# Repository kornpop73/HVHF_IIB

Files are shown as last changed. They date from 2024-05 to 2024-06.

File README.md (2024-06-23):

# HVHF_IIB
* Single-ended 65Vpp, 5ns amplifier with multiple output stages capable of driving capacitive loads up to 100pF. 
* This design is based on the circuit described in the 2005 paper by Holger Müller titled 'Fast High-Voltage Amplifiers for Driving Electro-Optic Modulators'.
* A link to the original paper can be found at the bottom of this page.
# High Voltage High Frequency IIB
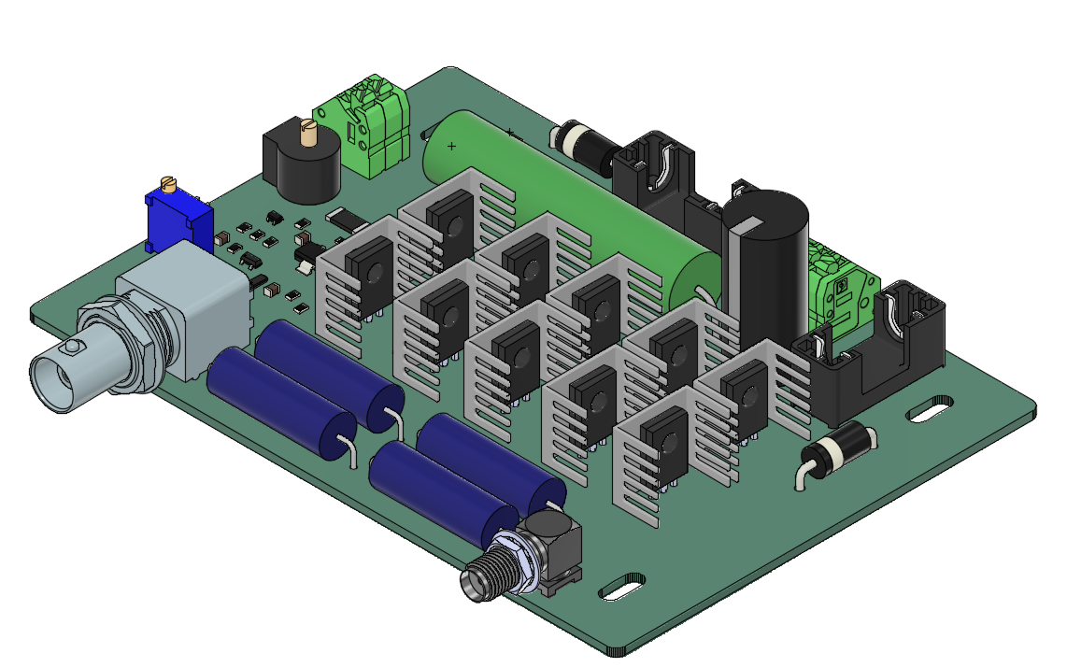
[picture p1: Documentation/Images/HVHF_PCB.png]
HVHF PCB

## Repository Contents

* [**/Design Files**](https://github.com/kornpop73/HVHF_IIB/tree/01/Design%20Files) - Contains all ECAD and MCAD files for this board
* [**/Documentation**](https://github.com/kornpop73/HVHF_IIB/tree/01/Documentation) - Contains all documentation related to this product (schematics, data sheets, test results et.
* [**/Production**](https://github.com/kornpop73/HVHF_IIB/tree/01/Production) - Contains all production files for this product (gerbers, BOMs, etc.)
## Documentation
Copies of documentation are also saved in this repository

* **[Sources](https://github.com/kornpop73/HVHF_IIB/blob/01/Documentation/Schematic%20Diagrams/Müller_Paper.pdf)** - Holger Müller,'Fast High-Voltage Amplifiers for Driving Electro-Optic Modulators'
* **[Bill of Materials](https://github.com/kornpop73/HVHF_IIB/blob/01/Production/BOM)**

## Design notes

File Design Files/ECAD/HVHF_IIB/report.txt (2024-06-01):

Warning: Width correction constrained.  The width correction value must be in the range of [0.000001 mm; 0.199999 mm] for the current design rules.
Plotted to 'C:\Users\kornelis\Desktop\Product Designs\HVHF_IIB\Design Files\ECAD\HVHF_IIB\HVHF_IIB-F_Cu.gbr'.
Plotted to 'C:\Users\kornelis\Desktop\Product Designs\HVHF_IIB\Design Files\ECAD\HVHF_IIB\HVHF_IIB-In1_Cu.gbr'.
Plotted to 'C:\Users\kornelis\Desktop\Product Designs\HVHF_IIB\Design Files\ECAD\HVHF_IIB\HVHF_IIB-In2_Cu.gbr'.
Plotted to 'C:\Users\kornelis\Desktop\Product Designs\HVHF_IIB\Design Files\ECAD\HVHF_IIB\HVHF_IIB-B_Cu.gbr'.
Plotted to 'C:\Users\kornelis\Desktop\Product Designs\HVHF_IIB\Design Files\ECAD\HVHF_IIB\HVHF_IIB-F_Paste.gbr'.
Plotted to 'C:\Users\kornelis\Desktop\Product Designs\HVHF_IIB\Design Files\ECAD\HVHF_IIB\HVHF_IIB-B_Paste.gbr'.
Plotted to 'C:\Users\kornelis\Desktop\Product Designs\HVHF_IIB\Design Files\ECAD\HVHF_IIB\HVHF_IIB-F_Silkscreen.gbr'.
Plotted to 'C:\Users\kornelis\Desktop\Product Designs\HVHF_IIB\Design Files\ECAD\HVHF_IIB\HVHF_IIB-B_Silkscreen.gbr'.
Plotted to 'C:\Users\kornelis\Desktop\Product Designs\HVHF_IIB\Design Files\ECAD\HVHF_IIB\HVHF_IIB-F_Mask.gbr'.
Plotted to 'C:\Users\kornelis\Desktop\Product Designs\HVHF_IIB\Design Files\ECAD\HVHF_IIB\HVHF_IIB-B_Mask.gbr'.
Plotted to 'C:\Users\kornelis\Desktop\Product Designs\HVHF_IIB\Design Files\ECAD\HVHF_IIB\HVHF_IIB-Edge_Cuts.gbr'.
Created Gerber job file 'C:\Users\kornelis\Desktop\Product Designs\HVHF_IIB\Design Files\ECAD\HVHF_IIB\HVHF_IIB-job.gbrjob'.
Info: Done.

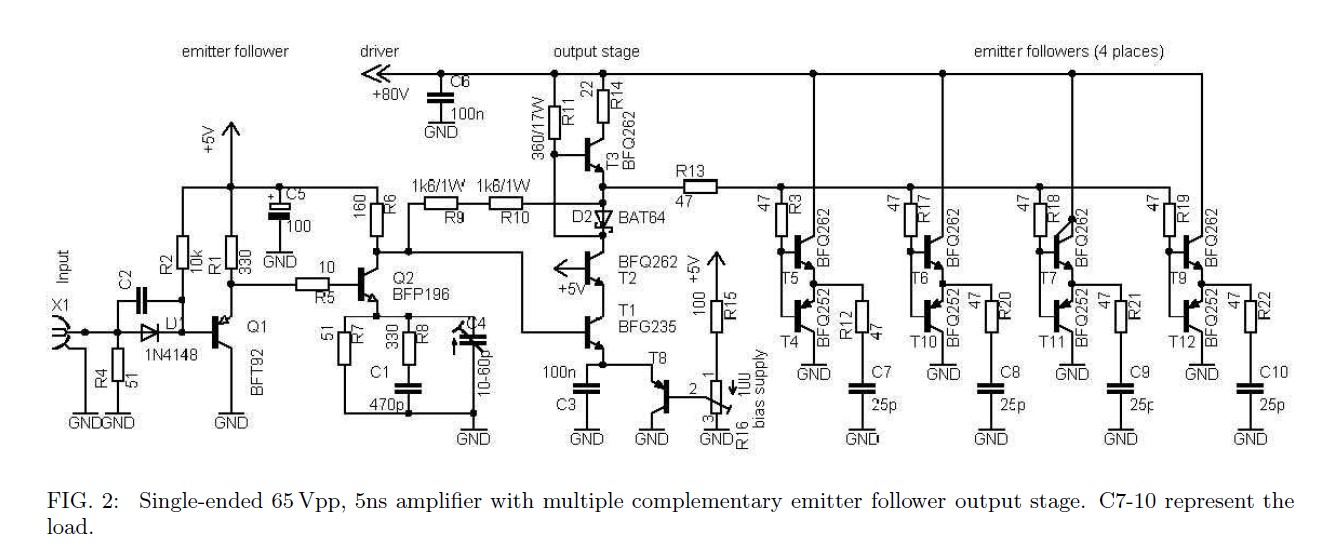
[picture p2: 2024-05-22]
Documentation/Images/IIB_Schematic.jpg

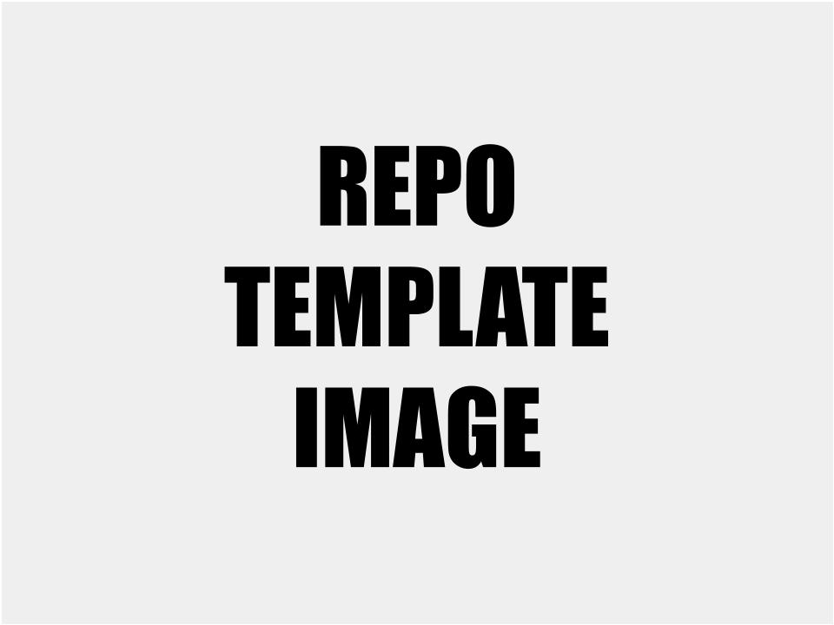
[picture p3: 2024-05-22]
Documentation/Images/Repository Template Sign.jpg

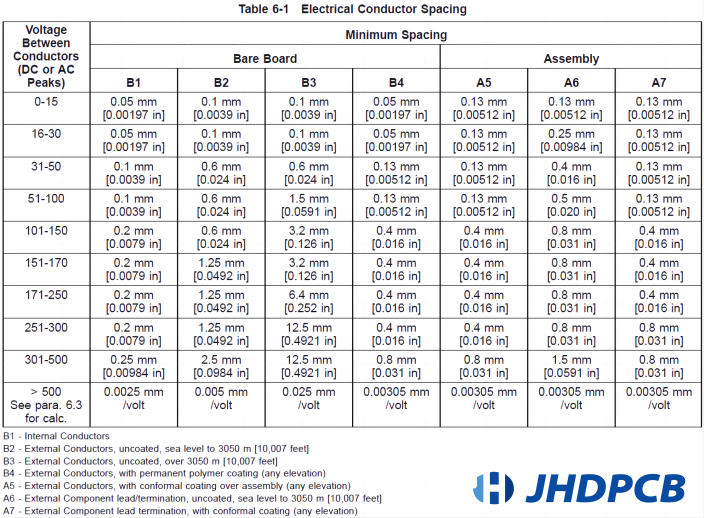
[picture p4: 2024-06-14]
Documentation/Data Sheets/criteria-that-govern-the-spacing-of-traces.png

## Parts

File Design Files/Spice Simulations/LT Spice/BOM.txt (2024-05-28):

--- Bill of Materials ---

Ref.	Mfg.	Part No.	Description
C1	--	--	capacitor, 470pF, 10V
C2	--	--	capacitor, 1µF, 10V
C3	--	--	capacitor, 100nF, 5V
C4	--	--	capacitor, 10pF, 10V
C5	--	--	capacitor, 100µF, 10V
C6	--	--	capacitor, 100nF, 200V
C7	--	--	capacitor, 25pF
C8	--	--	capacitor, 25pF
C9	--	--	capacitor, 25pF
C10	--	--	capacitor, 25pF
C11	--	--	capacitor, 100nF, 10V
C12	--	--	capacitor, 10µF, 200V
D1	OnSemi	1N4148	diode
D2	OnSemi	1N4148	diode
Q1	--	BFT92	bipolar transistor
Q2	--	BFP196	bipolar transistor
R1	--	--	resistor, 330, .125W%
R2	--	--	resistor, 10K, .125W
R3	--	--	resistor, 47, .125W
R4	--	--	resistor, 51, .125W
R5	--	--	resistor, 10, .125W
R6	--	--	resistor, 160, .5W
R7	--	--	resistor, 51, .125W
R8	--	--	resistor, 330, .125W
R9	--	--	resistor, 1.6K, 1W
R10	--	--	resistor, 1.6K, 1W
R11	--	--	resistor, 360
R12	--	--	resistor, 47, 5W
R13	--	--	resistor, 47, 5W
R14	--	--	resistor, 22
R15	--	--	resistor, 100, .5W
R16	--	--	resistor, 50, .5W
R17	--	--	resistor, 47, .125W
R18	--	--	resistor, 47, .125W
R19	--	--	resistor, 47, .125W
R20	--	--	resistor, 47, 5W
R21	--	--	resistor, 47, 5W
R22	--	--	resistor, 47, 5W
R23	--	--	resistor, 10, .125W
T1	--	NPN	bipolar transistor
T2	--	NPN	bipolar transistor
T3	--	NPN	bipolar transistor
T4	--	PNP	bipolar transistor
T5	--	NPN	bipolar transistor
T6	--	NPN	bipolar transistor
T7	--	NPN	bipolar transistor
T8	--	PNP	bipolar transistor
T9	--	NPN	bipolar transistor
T10	--	PNP	bipolar transistor
T11	--	PNP	bipolar transistor
T12	--	PNP	bipolar transistor

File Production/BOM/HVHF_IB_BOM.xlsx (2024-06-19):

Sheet: Digikey
Item # | Ref Des | Qty | Manufacturer | Mfg Part # | Description | Package | Digikey PN | Other vendor | Comments | Substitute
1 | Q2 | 1 | Infineon Technologies | BFP196WH6327XTSA1 | RF TRANS NPN 12V 7.5GHZ | SOT343-4 | BFP196WH6327XTSA1CT-ND (https://www.digikey.com/en/products/detail/infineon-technologies/BFP196WH6327XTSA1/2337768)
2 | T1 | 1 | NXP USA Inc. | BFU590GX | RF TRANS NPN 12V 8.5GHZ SOT223 | SC-73 | 568-11521-1-ND (https://www.digikey.com/en/products/detail/nxp-usa-inc/BFU590GX/4895819?s=N4IgTCBcDaIEYDMCuBWAnABgOYgLoF8g) |  | pin to pin replacement for BFG 235
3 | Q1 | 1 | Infineon Technologies | BFR92PE6327HTSA1 | RF TRANS NPN 15V 5GHZ SOT23-3 | SOT-23-3 | BFR92PE6327HTSA1CT-NDD (https://www.digikey.com/en/products/detail/infineon-technologies/BFR92PE6327HTSA1/1281557) |  | pin to pin replacement for BFT92
4 | T8 | 1 | Nexperia USA Inc. | PMBT2907A,235 | TRANS PNP 60V 0.6A TO236AB | SOT-23-3 | 1727-1884-1-ND (https://www.digikey.com/en/products/detail/nexperia-usa-inc/PMBT2907A-235/1157636) |  | Alternatives: BC807-40, MMBT5401
5 | T2, T3, T5, T6, T7,T9 | 6 | Philips Semiconductors | BFQ262 | NPN video transistors
6 | T4, T10, T11, T12 | 4 | Philips Semiconductors | BFQ252 | PNP video transistors
7 | R11 | 1 | RESI | PWWR0016F330RK9 | 330 Ohms ±1% 16W Through Hole Resistor Axial Wirewound | Axial | 4506-PWWR0016F330RK9-ND (https://www.digikey.com/en/products/detail/resi/PWWR0016F330RK9/22119934)
8 | R16 | 1 | Bourns Inc. | 3296W-1-101RLF | TRIMMER 100 OHM 0.5W PC PIN TOP |  | 118-3296W-1-101RLFCT-ND (https://www.digikey.com/en/products/detail/bourns-inc/3296W-1-101RLF/2535859)
9 | R12, R20-R22 | 4 | Vishay Dale | ALSR0547R00FE12 | RES 47 OHM 5W 1% AXIAL | AXIAL | ALSR5F-47-ND (https://www.digikey.com/en/products/detail/vishay-dale/ALSR0547R00FE12/257314) |  | 10 Ohm and 200 Ohm versions (https://www.digikey.com/en/products/detail/vishay-dale/ALSR0510R00FE12/257301)
10 | R9-R10 | 2 | Vishay Dale | CRCW25121K60JNEG | RES SMD 1.6K OHM 5% 1W 2512 | 2512 | 541-1.6KXCT-ND (https://www.digikey.com/en/products/detail/vishay-dale/CRCW25121K60JNEG/1173446)
11 | R15 | 1 | Stackpole Electronics Inc | RMCF0805FT100R | RES 100 OHM 1% 1/8W 0805 | 0805 | RMCF0805FT100RCT-ND (https://www.digikey.com/en/products/detail/stackpole-electronics-inc/RMCF0805FT100R/1760711)
12 | R5, R30-R31 | 3 | YAGEO | RC0805FR-0710RL | RES 10 OHM 1% 1/8W 0805 | 0805 | 311-10.0CRCT-ND (https://www.digikey.com/en/products/detail/yageo/RC0805FR-0710RL/727534)
13 | R1, R8 | 2 | Bourns Inc. | CR0805-JW-331ELF | RES SMD 330 OHM 5% 1/8W 0805 | 0805 | CR0805-JW-331ELFCT-ND (https://www.digikey.com/en/products/detail/bourns-inc/CR0805-JW-331ELF/3741034)
14 | R14 | 1 | Stackpole Electronics Inc | RMCF0805JT22R0 | RES 22 OHM 5% 1/8W 0805 | 0805 | RMCF0805JT22R0CT-ND (https://www.digikey.com/en/products/detail/stackpole-electronics-inc/RMCF0805JT22R0/1757897)
15 | R23 | 1 | Panasonic Electronic Components | ERJ-6ENF3600V | RES SMD 360 OHM 1% 1/8W 0805 | 0805 | P360CCT-ND (https://www.digikey.com/en/products/detail/panasonic-electronic-components/ERJ-6ENF3600V/1746493)
16 | R3, R13, R17-R19 | 5 | YAGEO | RC0805FR-0747RL | RES 47 OHM 1% 1/8W 0805 | 0805 | 311-47.0CRCT-ND (https://www.digikey.com/en/products/detail/yageo/RC0805FR-0747RL/727972)
17 | R2 | 1 | YAGEO | RC0805FR-0710KL | RES 10K OHM 1% 1/8W 0805 | 0805 | 311-10.0KCRCT-ND (https://www.digikey.com/en/products/detail/yageo/RC0805FR-0710KL/727535)
18 | R4, R7 | 2 | YAGEO | RC0805FR-0751RL | RES 51 OHM 1% 1/8W 0805 | 0805 | 311-51.0CRCT-ND (https://www.digikey.com/en/products/detail/yageo/RC0805FR-0751RL/728012)
19 | R6 | 1 | YAGEO | RC0805FR-07160RL | RES 160 OHM 1% 1/8W 0805 | 0805 | 311-160CRCT-ND (https://www.digikey.com/en/products/detail/yageo/RC0805FR-07160RL/727627)
20 | C1 | 1 | YAGEO | CC0805JRNPO9BN471 | CAP CER 470PF 50V C0G/NPO 0805 | 0805 | 311-1119-1-ND (https://www.digikey.com/en/products/detail/yageo/CC0805JRNPO9BN471/302853)
21 | C2-C3,C10-C11 | 4 | YAGEO | CC0805KRX7R9BB104 | 0.1 µF ±10% 50V Ceramic Capacitor X7R | 0805 | 311-1140-1-ND (https://www.digikey.com/en/products/detail/yageo/CC0805KRX7R9BB104/302874) |  |  | BC2772-ND (https://www.digikey.com/en/products/detail/vishay-beyschlag-draloric-bc-components/BFC280832659/3028990)
22 | C4 | 1 | Passive Plus | PPZC80003 | 8-80PF, 9.5MM TOP/BOTTOM ADJUST, |  | 4363-PPZC80003-ND (https://www.digikey.com/en/products/detail/passive-plus/PPZC80003/19235841?s=N4IgTCBcDaIApwFoGEAcAGTBmEBdAvkA)
23 | C5 | 1 | Murata Electronics | GRM31CR61A107MEA8L | CAP CER 100UF 10V X5R 1206 | 1206 | 490-GRM31CR61A107MEA8LCT-ND (https://www.digikey.com/en/products/detail/murata-electronics/GRM31CR61A107MEA8L/16033775)
24 | C6 | 1 | Panasonic Electronic Components | EEU-EE2C101 | CAP ALUM 100UF 20% 160V RADIAL | Radial, Can | P13622-ND (https://www.digikey.com/en/products/detail/panasonic-electronic-components/EEU-EE2C101/1245951)
25 | C7 | 1 | Würth Elektronik | 885342208002 | CAP CER 0.1UF 200V X7R 1206 | 1206 | 732-12081-1-ND (https://www.digikey.com/en/products/detail/w%C3%BCrth-elektronik/885342208002/9345893)
26 | D1 | 1 | Diodes Incorporated | 1N4148W-7-F | DIODE GEN PURP 100V 300MA SOD123 | SOD-123 | 1N4148W-FDICT-ND (https://www.digikey.com/en/products/detail/diodes-incorporated/1N4148W-7-F/814371)
27 | D2 | 1 | onsemi | MMBD701LT1G | DIODE SCHOTTKY 70V 200MW SOT23-3 | SOT-23-3 (TO-236) | MMBD701LT1GOSCT-ND (https://www.digikey.com/en/products/detail/onsemi/MMBD701LT1G/919574)
28 | D3-D4 | 2 | Vishay | 1N5408-E3/54 | DIODE GEN PURP 1KV 3A DO201AD | DO-201AD | 1N5408-E3/54GICT-ND (https://www.digikey.com/en/products/detail/vishay-general-semiconductor-diodes-division/1N5408-E3-54/76461)
29 | J1-J2, J5 | 3 | Phoenix Contact | 1984963 | TERM BLOCK 2POS 45DEG 3.5MM PCB |  | 277-6354-ND (https://www.digikey.com/en/products/detail/phoenix-contact/1984963/2513976?s=N4IgTCBcDaIIwE4AcAWBA2AzCAugXyA)
30 | J3 | 1 | Molex | 731375003 | CONN BNC RCPT R/A 50 OHM PCB |  | WM5514-ND (https://www.digikey.com/en/products/detail/molex/0731375003/1465136?s=N4IgTCBcDaIOwGYCMC4FYAMGEgLoF8g)
31 | J4 | 1 | TE Connectivity Linx | CONSMA002-L-ND | CONN SMA RCPT R/A 50 OHM PCB |  | CONSMA002-L-ND (https://www.digikey.com/en/products/detail/te-connectivity-linx/CONSMA002-L/1577206)
32 | HS1-HS10 | 10 | Advanced Thermal Solutions Inc. | ATS-PCB1025 | HEATSINK TO-126 BLACK |  | ATS2067-ND (https://www.digikey.com/en/products/detail/advanced-thermal-solutions-inc/ATS-PCB1025/5030446)
33 | F1-F2 | 2 | Keystone Electronics | 4527 | FUSE HLDR CARTRIDGE 250V 5A PCB |  | 36-4527-ND (https://www.digikey.com/en/products/detail/keystone-electronics/4527/8397)
34 | F1' | 1 | Bel Fuse Inc. | 5ST 2-R | FUSE GLASS 2A 250VAC 5X20MM |  | 507-1249-ND (https://www.digikey.com/en/products/detail/bel-fuse-inc/5ST-2-R/1009021)
35 | F2' | 1 | Bel Fuse Inc. | 5ST 100-R | FUSE GLASS 100MA 250VAC 5X20MM |  | 507-1238-ND (https://www.digikey.com/en/products/detail/bel-fuse-inc/5ST-100-R/1009010)

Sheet: JLC_BOM
Comment | Designator | Footprint | LCSC Part Number
RF TRANS NPN 12V 7.5GHZ | Q2 | SOT343-4 | C3028874
RF TRANS NPN 12V 8.5GHZ SOT223 | T1 | SC-73 | DNP
RF TRANS NPN 25V 650MHZ SOT23-3 | Q1 | SOT-23-3 | C606059
TRANS PNP 60V 0.6A TO236AB | T8 | SOT-23-3 | C8665
NPN video transistors | T5,T2,T6,T7,T9,T3 |  | DNP
PNP video transistors | T4,T12,T11,T10 |  | DNP
330 Ohms ±1% 16W Through Hole Resistor Axial Wirewound | R11 | AXIAL | C20417286
TRIMMER 100 OHM 0.5W PC PIN TOP | R16 |  | DNP
RES 47 OHM 5W 1% AXIAL | R22,R12,R21,R20 | AXIAL | DNP
RES SMD 1.6K OHM 1% 1W 2512 | R10,R9 | 2512 | C5126121
RES 100 OHM 1% 1/8W 0805 | R15 | 0805 | C237122
RES 10 OHM 1% 1/8W 0805 | R31,R5,R30 | 0805 | C96347
RES SMD 330 OHM 1% 1/8W 0805 | R1, R8 | 0805 | C105878
RES 22 OHM 1% 1/8W 0805 | R14 | 0805 | C728646
RES SMD 360 OHM 1% 1/8W 0805 | R23 | 0805 | C228768
RES 47 OHM 1% 1/8W 0805 | R18,R13,R19,R17,R3 | 0805 | C114541
RES 10K OHM 1% 1/8W 0805 | R2 | 0805 | C84376
RES 51 OHM 1% 1/8W 0805 | R4, R7 | 0805 | C114537
RES 160 OHM 0.1% 1/8W 0805 | R6 | 0805 | C706215
CAP CER 470PF 50V C0G/NPO 0805 | C1 | 0805 | C62771
0.1 µF ±10% 50V Ceramic Capacitor X7R | C11,C2,C3,C10 | 0805 | C49678
8-80PF, 9.5MM TOP/BOTTOM ADJUST, | C4
CAP CER 100UF 10V X5R 1206 | C5 | 1206 | C883598
CAP ALUM 100UF 20% 160V RADIAL | C6 | Radial, Can | DNP
CAP CER 0.1UF 200V X7R 1206 | C7 | 1206 | C113894
DIODE GEN PURP 100V 300MA SOD123 | D1 | SOD-123 | C83528
DIODE SCHOTTKY 70V 200MW SOT23-3 | D2 | SOT-23-3 (TO-236) | C232601
DIODE GEN PURP 1KV 3A DO201AD | D3,D4 | DO-201AD | C143658
TERM BLOCK 2POS 45DEG 3.5MM PCB | J2,J5,J1 |  | DNP
CONN BNC RCPT R/A 50 OHM PCB | J3 |  | DNP
CONN SMA RCPT R/A 50 OHM PCB | J4 |  | DNP
HEATSINK TO-126 BLACK | HS4,HS7,HS6,HS5,HS10,HS9,HS8,HS3,HS1,HS2 |  | DNP
FUSE HLDR CARTRIDGE 250V 5A PCB | F2,F1 |  | DNP
Testpoints pads | TP6,TP4,TP7,TP5,TP3,TP2,TP1 |  | DNP
PCB footprint | PCB1 |  | DNP
Mounting Hole | H1 |  | DNP
Bard Logo | LOGO1 |  | DNP

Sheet: JLC_CPL
Designator | Mid X | Mid Y | Layer | Rotation
C1 | 96 | -111.863 | top | -90
C2 | 110.67 | -115.9005 | top | 90
C3 | 116 | -102.8255 | top | 90
C4 | 95 | -92.46 | top | 180
C5 | 109.0625 | -63.613 | top | 180
C6 | 175.5 | -74.02785 | top | -90
C7 | 120 | -87.6875 | top | 90
C10 | 135 | -107.2755 | top | 90
C11 | 104.5 | -103.215891 | top | -90
D1 | 107.42 | -115.713 | top | 90
D2 | 113.7975 | -87.0348 | top | 0
D3 | 202 | -95.62 | top | 90
D4 | 113.38 | -59 | top | 0
F1 | 190.25 | -69.5 | top | 90
F2 | 144 | -61 | top | 0
H1 | 92 | -112 | top | 0
HS1 | 127.3 | -111.022453 | top | -90
HS2 | 127.3 | -93.613 | top | -90
HS3 | 189.795 | -110.613 | top | -90
HS4 | 189.795 | -93.613 | top | -90
HS5 | 174.795 | -93.613 | top | -90
HS6 | 174.795 | -110.613 | top | -90
HS7 | 158.445 | -93.613 | top | -90
HS8 | 158.445 | -110.613 | top | -90
HS9 | 143.445 | -93.613 | top | -90
HS10 | 143.445 | -110.613 | top | -90
J1 | 173.900001 | -60.5 | top | 180
J2 | 162.5416 | -60.6206 | top | 180
J3 | 111 | -129.75 | top | 180
J4 | 192 | -138.84 | top | 0
J5 | 93 | -81.5 | top | -90
PCB1 | 150 | -100 | top | 0
Q1 | 103 | -112.613 | top | 0
Q2 | 97.675 | -102.313 | top | -90
R1 | 98.75 | -111.863 | top | 90
R2 | 113.5 | -114.363 | top | -90
R3 | 183 | -90.363 | top | -90
R4 | 116.75 | -115.863 | top | 90
R5 | 101.4 | -107.032891 | top | 90
R6 | 101.45 | -100.213 | top | 90
R7 | 98.75 | -107.032891 | top | -90
R8 | 96 | -107.113 | top | -90
R9 | 106 | -95.113 | top | 180
R10 | 114.5 | -95.113 | top | 180
R11 | 135.8 | -77.113 | top | -90
R12 | 155 | -129 | top | 0
R13 | 135 | -95.363 | top | -90
R14 | 120.25 | -92.613 | top | -90
R15 | 94 | -124 | top | 0
R16 | 91.7 | -119 | top | 0
R17 | 167 | -90.363 | top | -90
R18 | 151 | -90.363 | top | -90
R19 | 135 | -90.363 | top | -90
R20 | 155 | -139 | top | 0
R21 | 151 | -139 | top | 180
R22 | 151 | -129 | top | 180
R23 | 91.25 | -70.150001 | top | -90
R30 | 109 | -99.363 | top | 180
R31 | 135 | -113.113 | top | -90
T1 | 110.06 | -105.565891 | top | -90
T2 | 124.5 | -110.613 | top | 90
T3 | 124.5 | -93.613 | top | 90
T4 | 186.75 | -110.613 | top | 90
T5 | 186.75 | -93.613 | top | 90
T6 | 171.75 | -93.613 | top | 90
T7 | 155.5 | -93.613 | top | 90
T8 | 116.75 | -108.613 | top | 90
T9 | 140.5 | -93.613 | top | 90
T10 | 171.75 | -110.613 | top | 90
T11 | 155.5 | -110.613 | top | 90
T12 | 140.5 | -110.613 | top | 90

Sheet: KiCad raw
Id | Designator | Footprint | Quantity | Designation | Supplier and ref
1 | HS4,HS7,HS6,HS5,HS10,HS9,HS8,HS3,HS1,HS2 | ATS_PCB1025 | 10 | ~
2 | C11,C2,C3,C10 | C_0805_2012Metric_Pad1.18x1.45mm_HandSolder | 4 | 0.1u
3 | R15 | R_0805_2012Metric_Pad1.20x1.40mm_HandSolder | 1 | 100R
4 | F2,F1 | FUSE_4527 | 2 | Fuse
5 | T5,T2,T6,T7,T9,T3 | TO126AV | 6 | BFQ262
6 | D3,D4 | D_DO-201AD_P15.24mm_Horizontal | 2 | 1N5408
7 | J2,J5,J1 | CONN_1984963 | 3 | 1984963
8 | J4 | LINX_CONSMA002-L | 1 | CONSMA002-L
9 | R22,R12,R21,R20 | RES_ALSR05_VIS | 4 | 47
10 | T4,T12,T11,T10 | TO126AV | 4 | BFQ252
11 | D1 | SOD123_MCC-M | 1 | 1N4148W
12 | TP6,TP4,TP7,TP5,TP3,TP2,TP1 | TestPoint_Pad_D1.0mm | 7 | TestPoint
13 | R31,R5,R30 | R_0805_2012Metric_Pad1.20x1.40mm_HandSolder | 3 | 10
14 | R1,R8 | R_0805_2012Metric_Pad1.20x1.40mm_HandSolder | 2 | 330
15 | D2 | SOT-23_ONS | 1 | BAT64
16 | C1 | C_0805_2012Metric_Pad1.18x1.45mm_HandSolder | 1 | 470p
17 | R14 | R_0805_2012Metric_Pad1.20x1.40mm_HandSolder | 1 | 22
18 | R23 | R_0805_2012Metric_Pad1.20x1.40mm_HandSolder | 1 | 360
19 | T8 | SOT23_NXP | 1 | ~
20 | R18,R13,R19,R17,R3 | R_0805_2012Metric_Pad1.20x1.40mm_HandSolder | 5 | 47
21 | C7 | C_1206_3216Metric_Pad1.33x1.80mm_HandSolder | 1 | 0.1u
22 | C4 | PPZC80003 | 1 | C_Trim
23 | R10,R9 | RC2512N_VIS-M | 2 | 1k6
24 | Q1 | SOT-23_ONS | 1 | PNP
25 | R11 | PWWR0016 | 1 | 360
26 | PCB1 | PCB_EC1U | 1 | ~EC1U
27 | R2 | R_0805_2012Metric_Pad1.20x1.40mm_HandSolder | 1 | 10k
28 | R4,R7 | R_0805_2012Metric_Pad1.20x1.40mm_HandSolder | 2 | 51
29 | H1 | Pin_D1.4mm_L8.5mm_W2.8mm_FlatFork | 1 | MountingHole_Pad
30 | C6 | CAP_EEUED_125X25_PAN | 1 | 100u
31 | R16 | POT_3296W | 1 | R_Potentiometer_Trim
32 | C5 | C_1206_3216Metric_Pad1.33x1.80mm_HandSolder | 1 | 100u
33 | T1 | SOT-223 | 1 | BFU590G
34 | R6 | R_0805_2012Metric_Pad1.20x1.40mm_HandSolder | 1 | 160
35 | Q2 | TRANS_BFP196E6327HTSA1_INF | 1 | BFP196E6327HTSA1
36 | J3 | CONN_73137-5003_MOL | 1 | 731375003
37 | LOGO1 | LOGO_M | 1 | ~

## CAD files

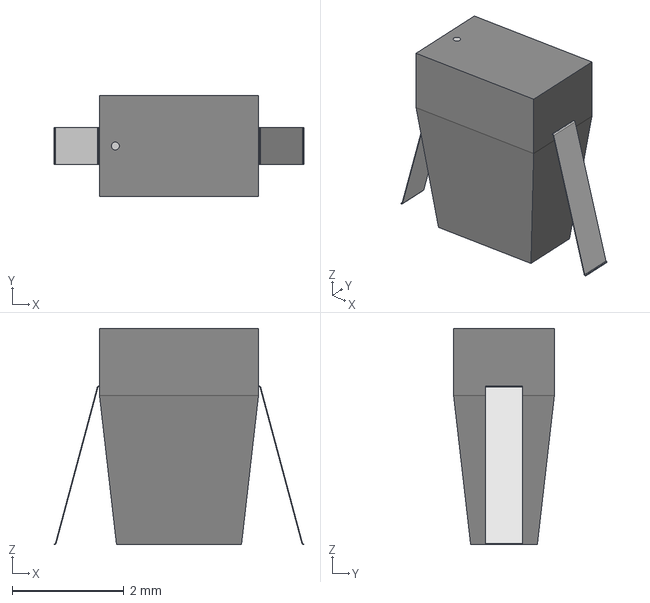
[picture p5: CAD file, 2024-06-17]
Design Files/MCAD/3D models/SOD123_MCC.step
4.47 x 1.80 x 3.86 mm

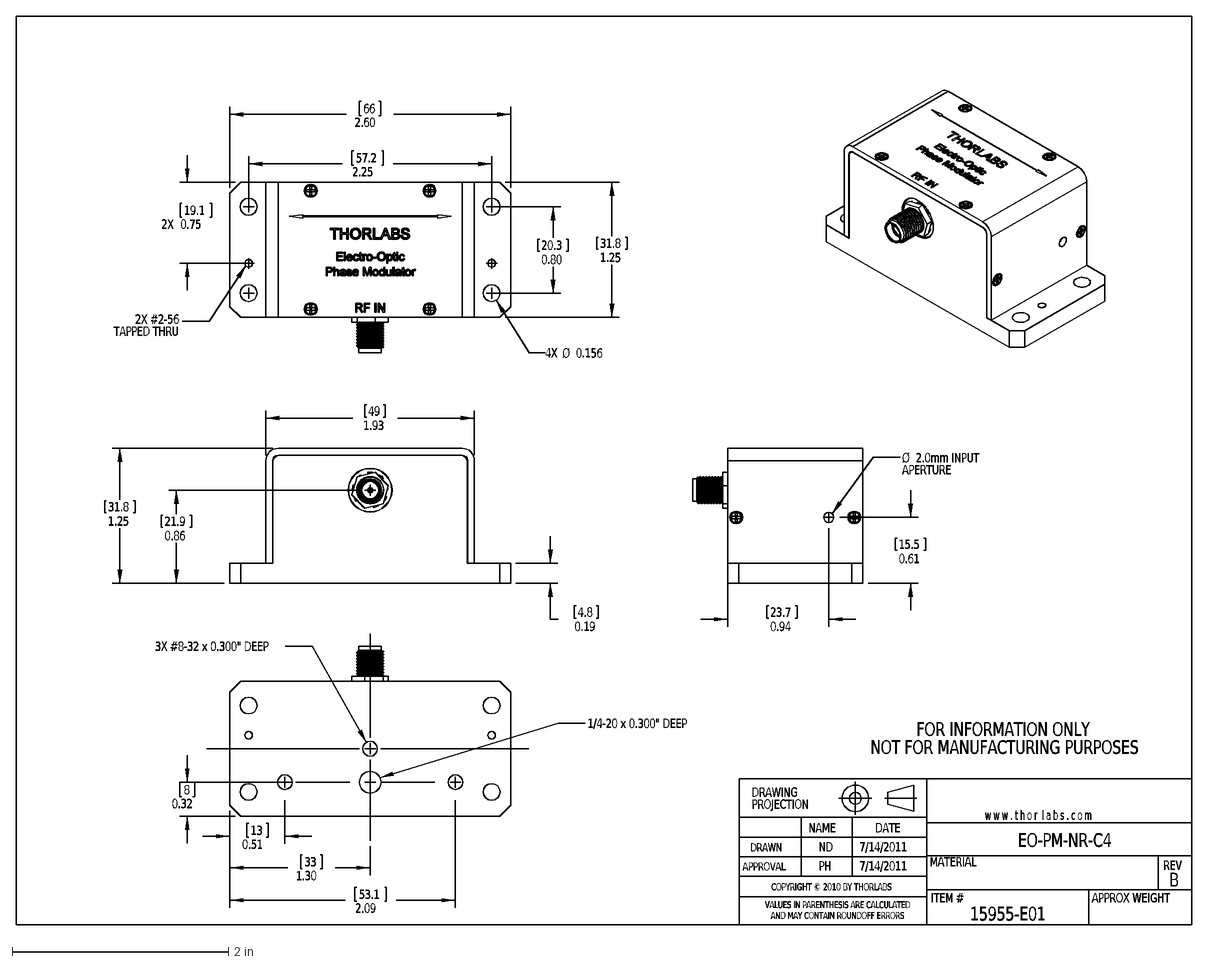
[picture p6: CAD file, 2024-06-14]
Documentation/Data Sheets/EOPMNRC4SupportDocumentation (1)/EO-PM-NR-C4-AutoCADDXF.dxf
B
15955-E01
MATERIAL
DRAWN
APPROVAL
REV
ND
PH
7/14/2011
DATE
w w w . t h o r l a b s . c o m
ITEM #
APPROX WEIGHT
VALUES IN PARENTHESIS ARE CALCULATED
AND MAY CONTAIN ROUNDOFF ERRORS
DRAWING
PROJECTION
NAME
FOR INFORMATION ONLY
NOT FOR MANUFACTURING PURPOSES
COPYRIGHT © 2010 BY THORLABS
EO-PM-NR-C4
0.19
4.8
1.25
31.8
0.86
21.9
1.93
49
0.94
23.7
0.61
15.5
Ø
2.0mm INPUT
APERTURE
0.80
20.3
2X
19.1
0.75
66
2.60
57.2
2.25
4X
0.156
2X #2-56
TAPPED THRU
8
0.32
13
0.51
33
1.30
53.1
2.09
3X #8-32 x 0.300" DEEP
1/4-20 x 0.300" DEEP

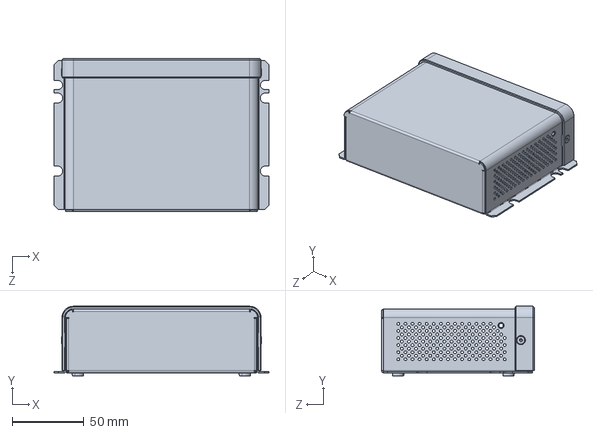
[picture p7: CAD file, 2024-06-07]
EC1USupportDocumentation/EC1U-Step.step
150.0 x 48.5 x 106.7 mm

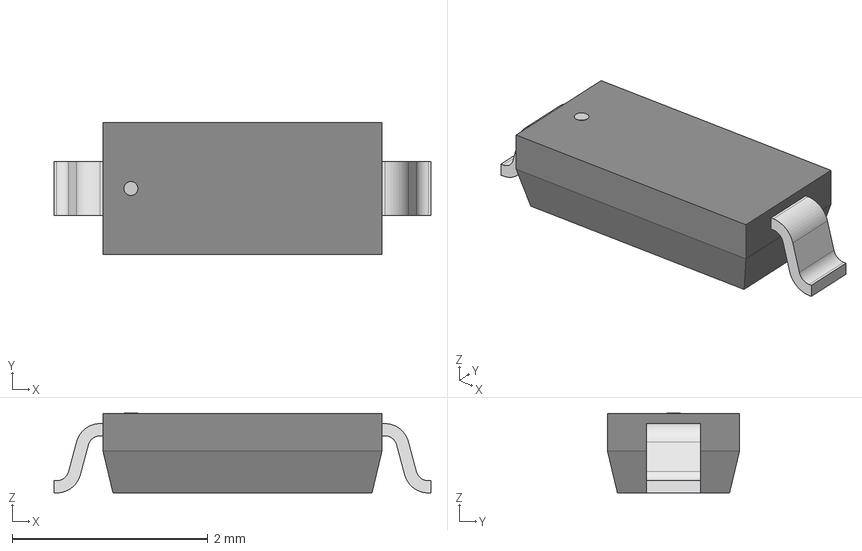
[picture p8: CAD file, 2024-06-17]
Design Files/MCAD/3D models/SOD123_DIO.step
3.85 x 1.35 x 0.815 mm

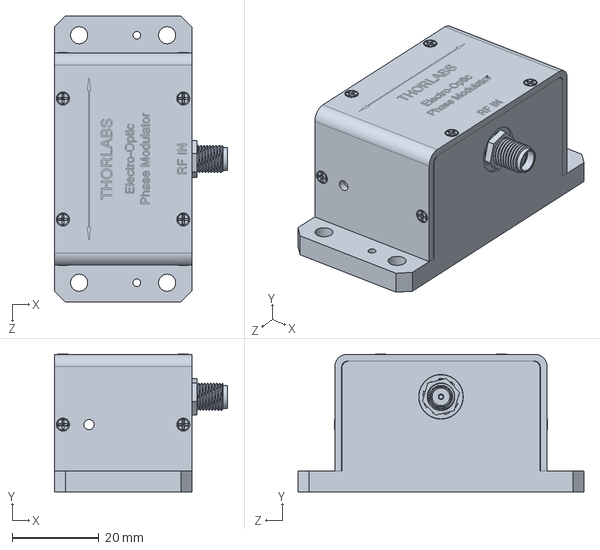
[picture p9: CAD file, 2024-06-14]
Documentation/Data Sheets/EOPMNRC4SupportDocumentation (1)/EO-PM-NR-C4-Solidworks.sldprt
40.0 x 31.8 x 66.0 mm

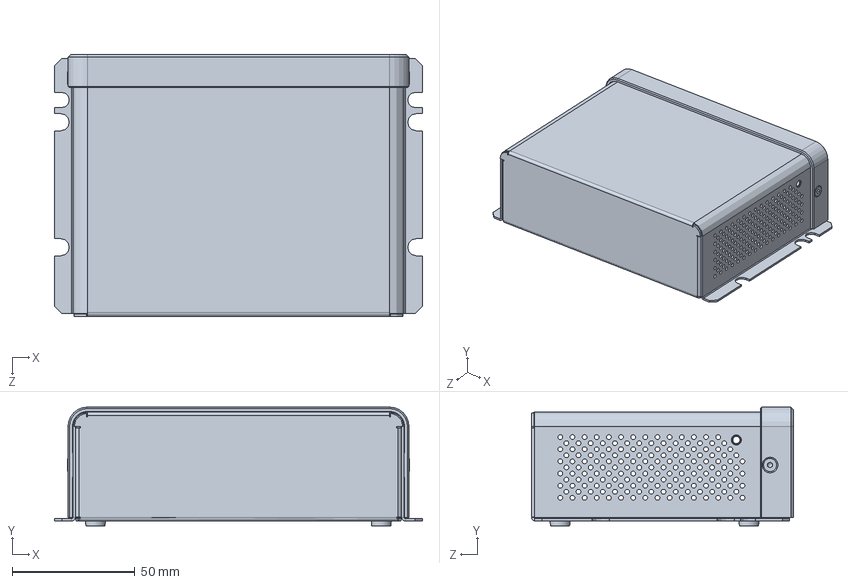
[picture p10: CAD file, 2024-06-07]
EC1USupportDocumentation/EC1U-Solidworks.sldprt
150.0 x 48.5 x 106.7 mm

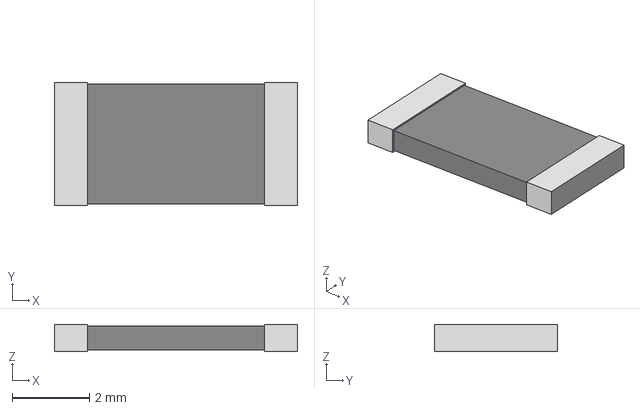
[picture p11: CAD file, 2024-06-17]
Design Files/MCAD/3D models/RC2512N_VIS.step
6.30 x 3.20 x 0.711 mm

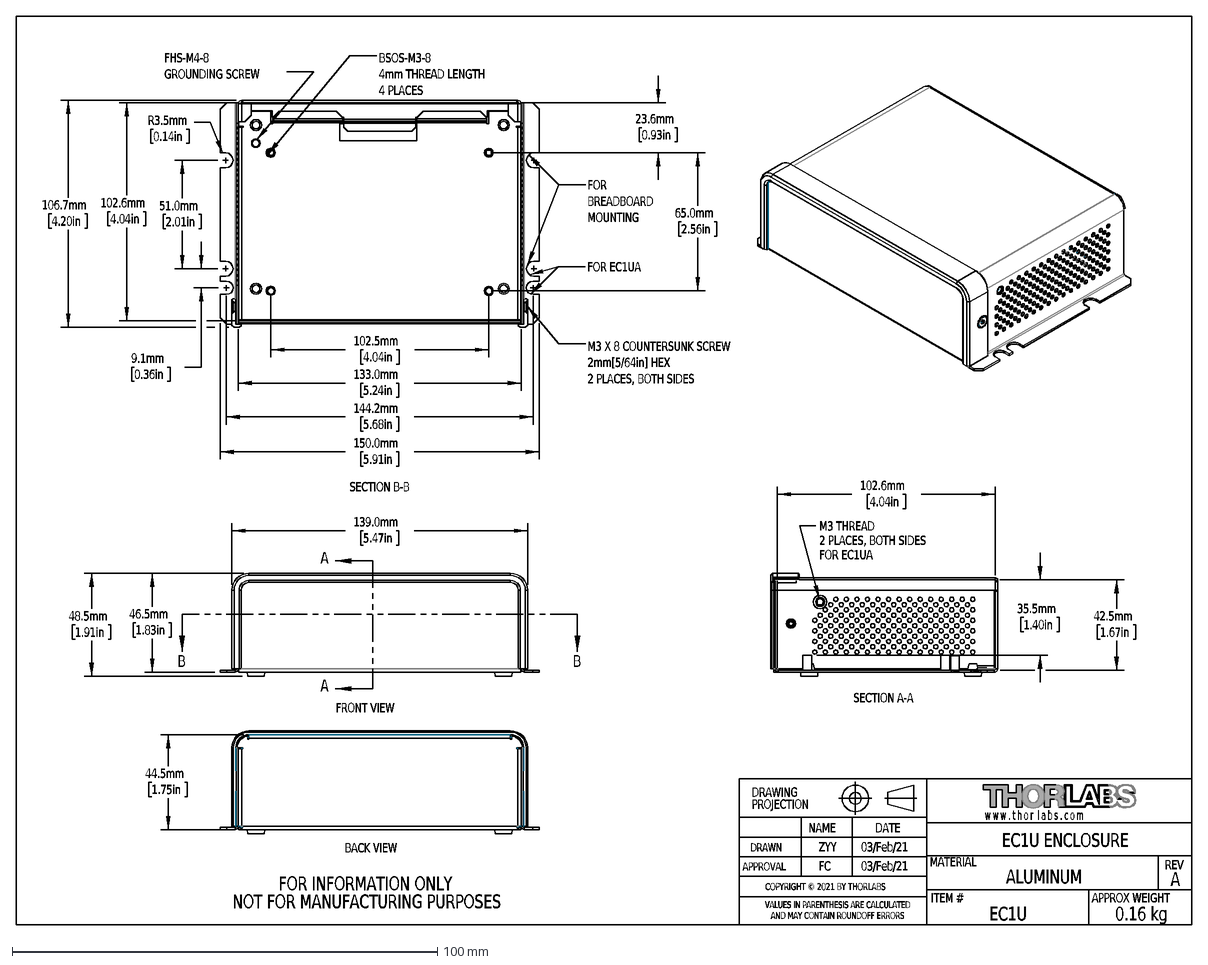
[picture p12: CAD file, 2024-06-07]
EC1USupportDocumentation/EC1U-AutoCADDXF.dxf
A
EC1U
MATERIAL
DRAWN
APPROVAL
REV
ZYY
FC
03/Feb/21
DATE
w w w . t h o r l a b s . c o m
ITEM #
APPROX WEIGHT
ALUMINUM
0.16 kg
VALUES IN PARENTHESIS ARE CALCULATED
AND MAY CONTAIN ROUNDOFF ERRORS
DRAWING
PROJECTION
NAME
FOR INFORMATION ONLY
NOT FOR MANUFACTURING PURPOSES
EC1U ENCLOSURE
COPYRIGHT © 2021 BY THORLABS
44.5mm
1.75in
BACK VIEW
46.5mm
1.83in
48.5mm
1.91in
139.0mm
5.47in
FRONT VIEW
B
M3 THREAD
2 PLACES, BOTH SIDES
FOR EC1UA
35.5mm
1.40in
42.5mm
1.67in
102.6mm
4.04in
SECTION A-A
102.5mm
65.0mm
2.56in
23.6mm
0.93in
9.1mm
0.36in
150.0mm
5.91in
106.7mm
4.20in
R3.5mm
0.14in
51.0mm
2.01in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

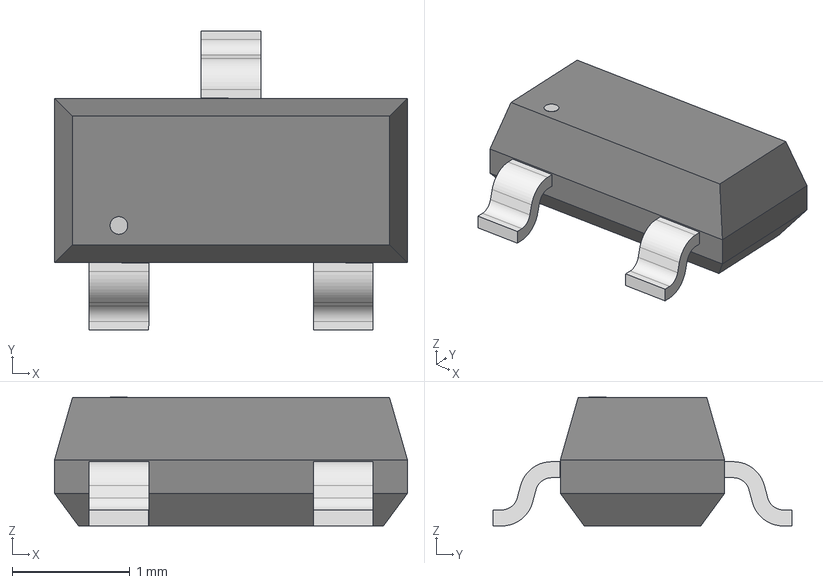
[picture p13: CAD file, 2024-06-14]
Design Files/MCAD/3D models/SOT23_INF.step
3.00 x 2.54 x 1.09 mm

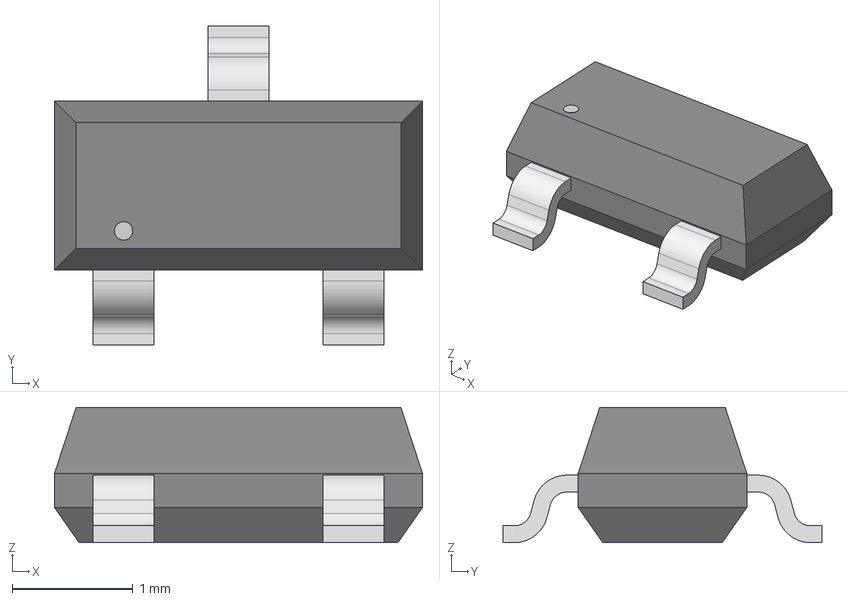
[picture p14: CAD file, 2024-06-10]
Design Files/MCAD/3D models/SOT-23_ONS.step
3.05 x 2.64 x 1.12 mm

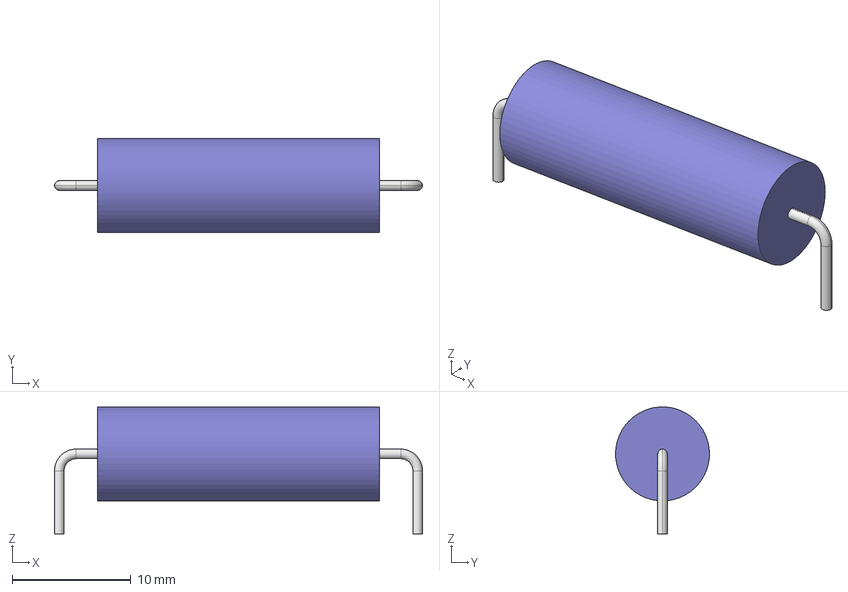
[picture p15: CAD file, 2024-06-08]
Design Files/MCAD/3D models/RES_ALSR05_VIS.step
31.0 x 7.92 x 10.7 mm

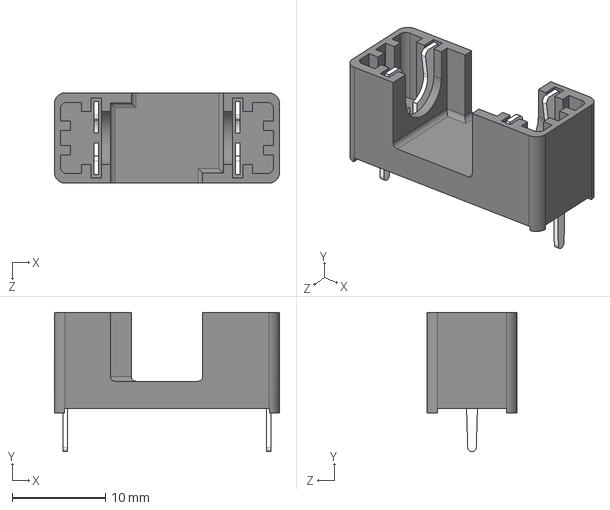
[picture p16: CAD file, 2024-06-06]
Design Files/MCAD/3D models/4527.step
24.2 x 15.0 x 9.70 mm

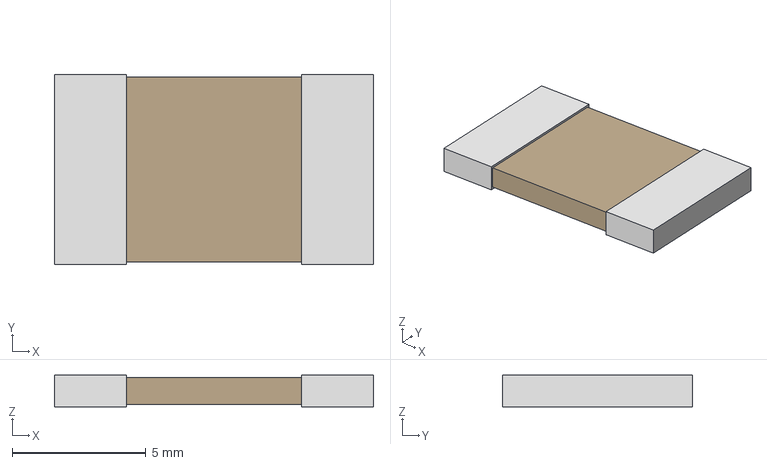
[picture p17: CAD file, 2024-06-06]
Design Files/MCAD/3D models/RES_3560_TEC.step
11.9 x 7.11 x 1.19 mm

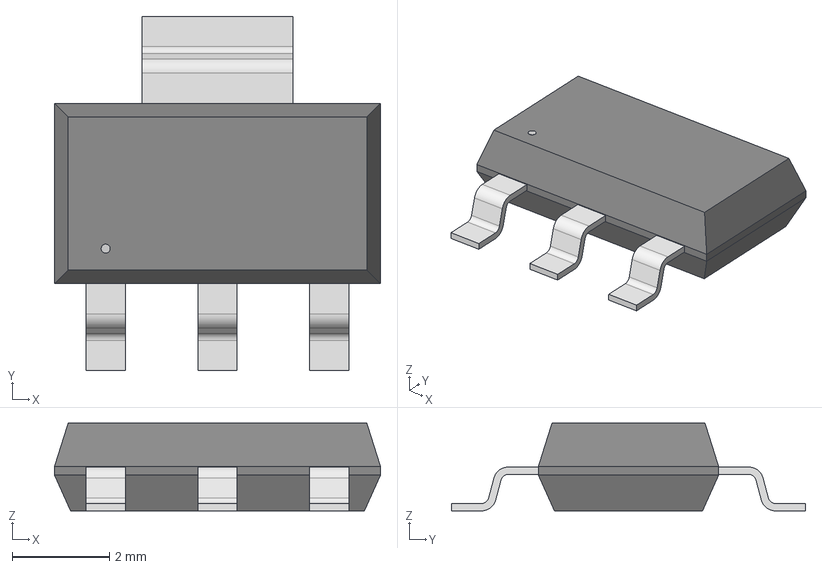
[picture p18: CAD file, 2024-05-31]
Design Files/MCAD/3D models/SC-73_SOT223_NXP.step
6.71 x 7.29 x 1.81 mm

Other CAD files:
Design Files/MCAD/3D models/SOT23_NXP.step
Design Files/MCAD/3D models/PWWR0016F330RK9 v2.step
Design Files/MCAD/3D models/PPZC80003.step
Design Files/MCAD/3D models/1984963.stp
Design Files/MCAD/3D models/3296W-1-101RLF.step
Design Files/MCAD/3D models/731375003.stp
Design Files/MCAD/3D models/ATS-PCB1025.step
Design Files/MCAD/3D models/CAP_EEUED_125X25_PAN.step
Design Files/MCAD/3D models/CONSMA002-L.step
Design Files/MCAD/3D models/CR_BAS70-02V_INF.step
Design Files/MCAD/3D models/GRM31CR61A107MEA8L.step
Design Files/MCAD/3D models/T0-126.step

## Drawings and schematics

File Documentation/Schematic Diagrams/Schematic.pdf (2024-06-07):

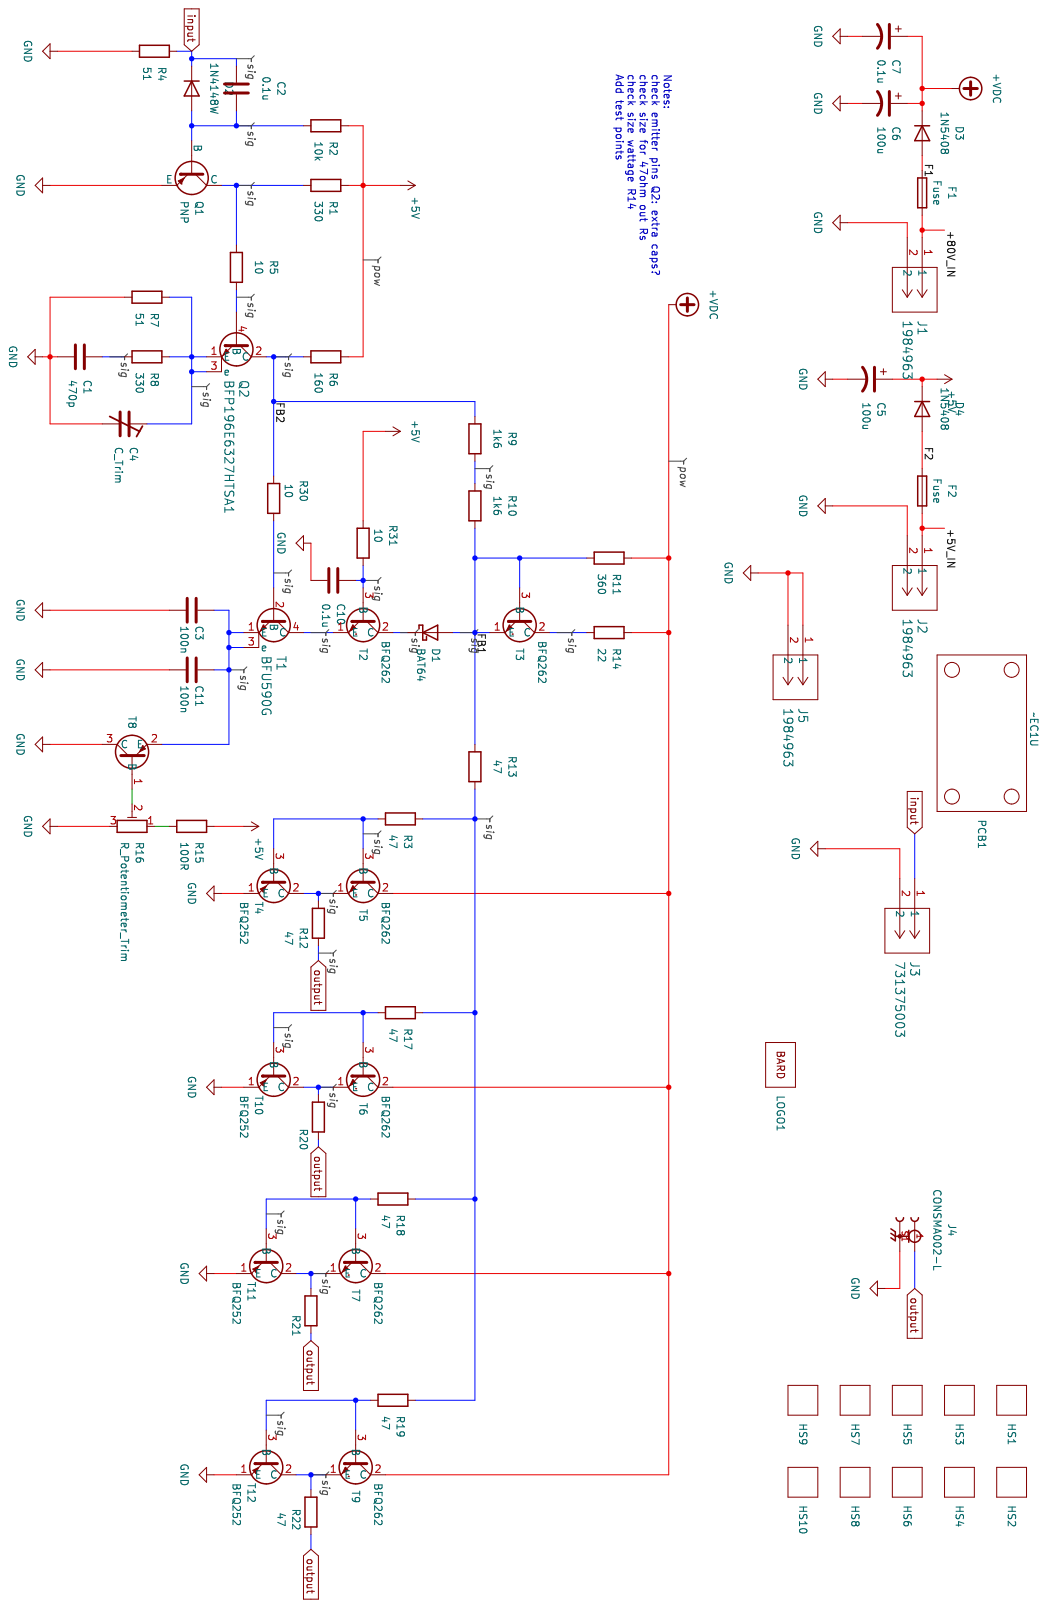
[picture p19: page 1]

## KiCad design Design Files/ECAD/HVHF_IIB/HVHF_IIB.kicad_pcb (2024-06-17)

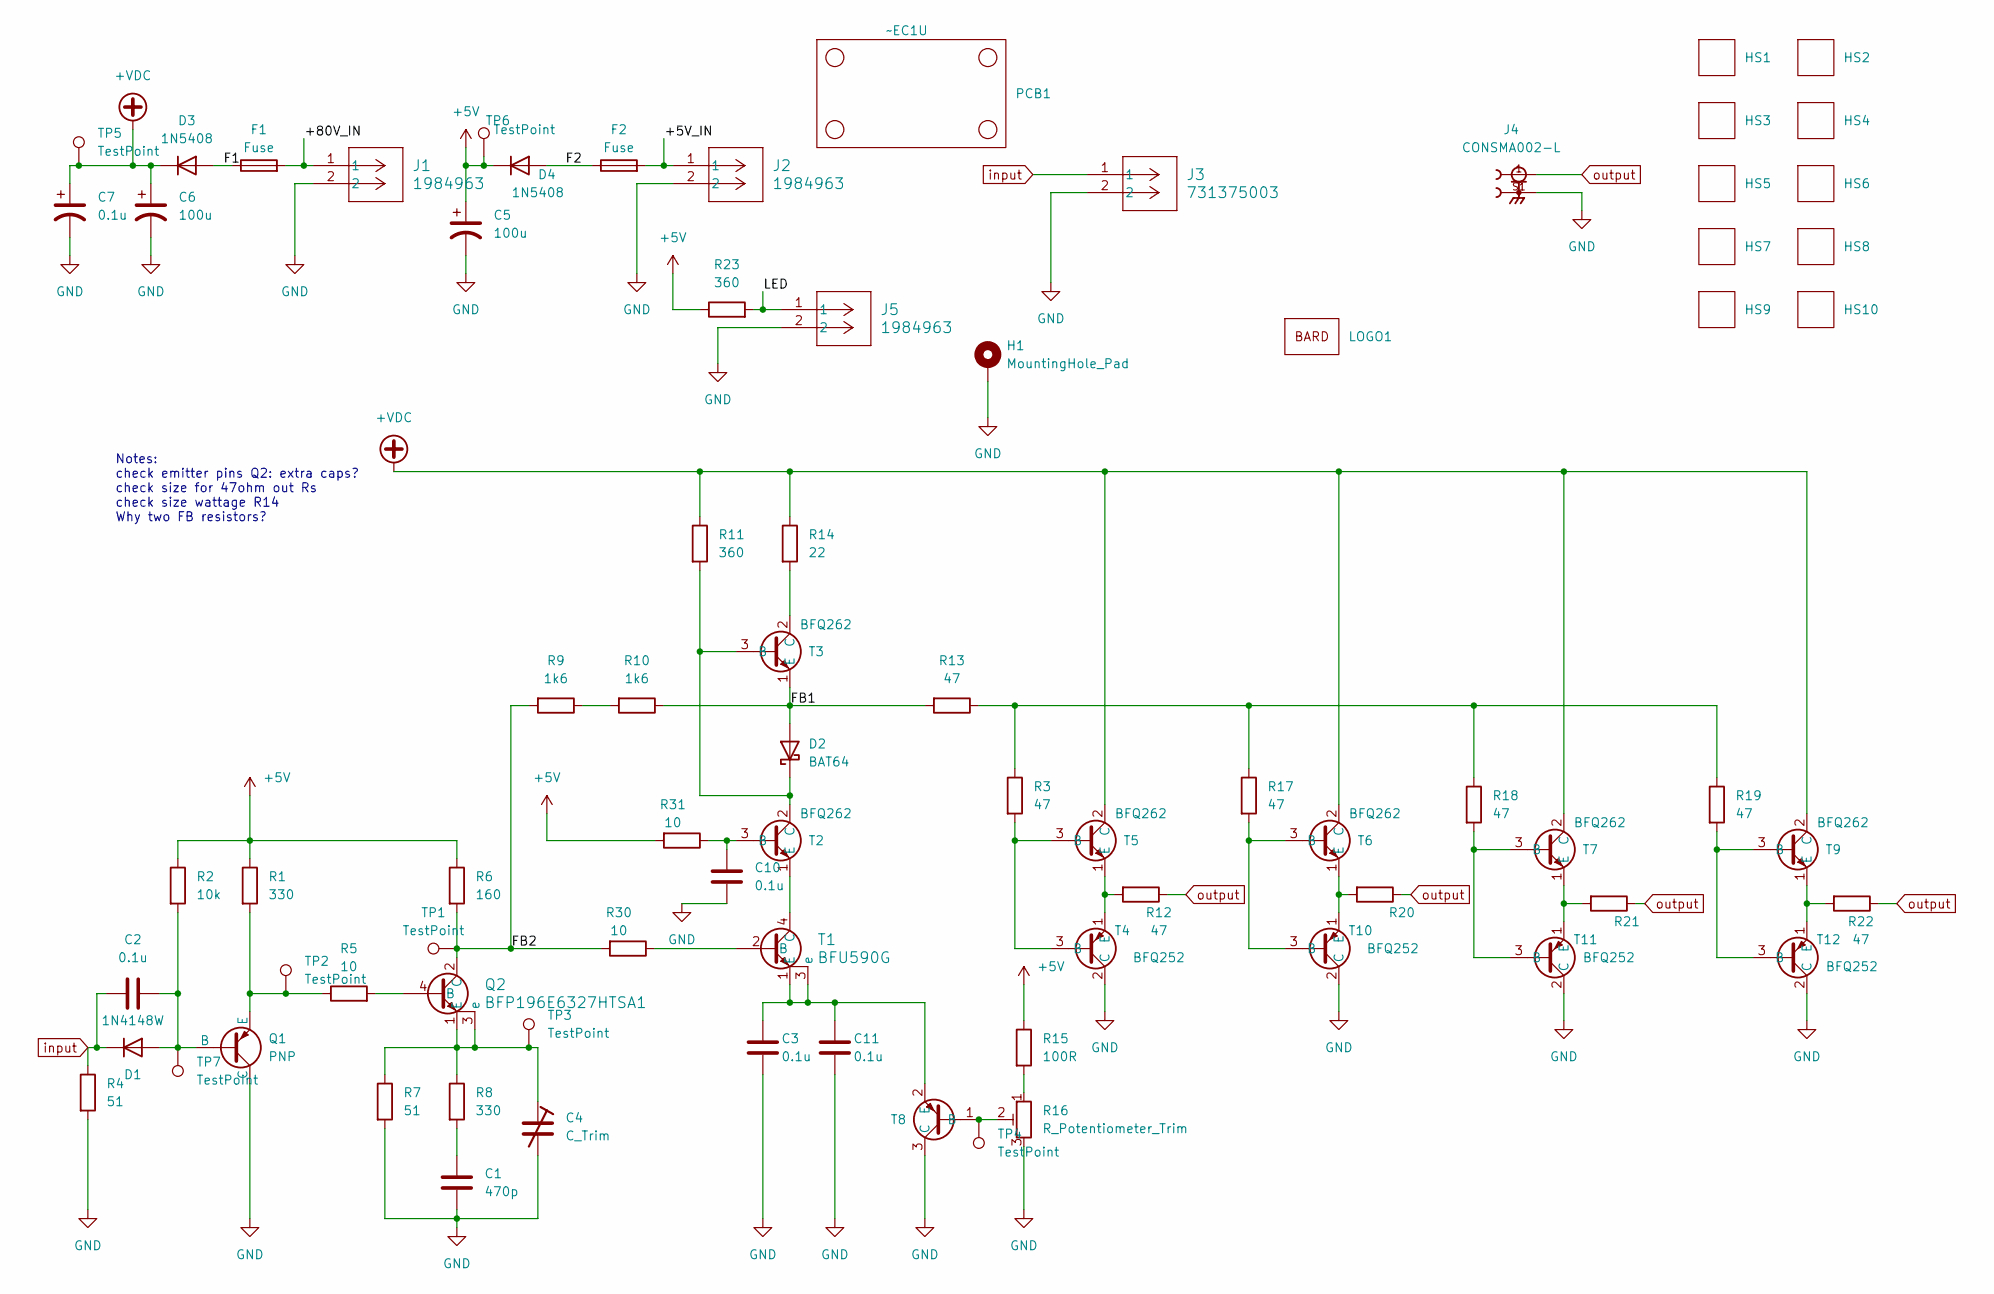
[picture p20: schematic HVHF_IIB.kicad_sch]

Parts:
C1: 470p; C_0805_2012Metric_Pad1.18x1.45mm_HandSolder
C2, C3, C10, C11: 0.1u; C_0805_2012Metric_Pad1.18x1.45mm_HandSolder
C4: C_Trim; PPZC80003
C5: 100u; C_1206_3216Metric_Pad1.33x1.80mm_HandSolder
C6: 100u; CAP_EEUED_125X25_PAN
C7: 0.1u; C_1206_3216Metric_Pad1.33x1.80mm_HandSolder
D1: 1N4148W; SOD123_MCC-M
D2: BAT64; SOT-23_ONS
D3, D4: 1N5408; D_DO-201AD_P15.24mm_Horizontal
F1, F2: Fuse; FUSE_4527
H1: MountingHole_Pad; Pin_D1.4mm_L8.5mm_W2.8mm_FlatFork
HS1, HS2, HS3, HS4, HS5, HS6, HS7, HS8, HS9, HS10: ATS_PCB1025
J1, J2, J5: 1984963; CONN_1984963
J3: 731375003; CONN_73137-5003_MOL
J4: CONSMA002-L; LINX_CONSMA002-L
LOGO1: LOGO_M
PCB1: ~EC1U; PCB_EC1U
Q1: PNP; SOT-23_ONS
Q2: BFP196E6327HTSA1; TRANS_BFP196E6327HTSA1_INF
R1, R8: 330; R_0805_2012Metric_Pad1.20x1.40mm_HandSolder
R2: 10k; R_0805_2012Metric_Pad1.20x1.40mm_HandSolder
R3, R13, R17, R18, R19: 47; R_0805_2012Metric_Pad1.20x1.40mm_HandSolder
R4, R7: 51; R_0805_2012Metric_Pad1.20x1.40mm_HandSolder
R5, R30, R31: 10; R_0805_2012Metric_Pad1.20x1.40mm_HandSolder
R6: 160; R_0805_2012Metric_Pad1.20x1.40mm_HandSolder
R9, R10: 1k6; RC2512N_VIS-M
R11: 360; PWWR0016
R12, R20, R21, R22: 47; RES_ALSR05_VIS
R14: 22; R_0805_2012Metric_Pad1.20x1.40mm_HandSolder
R15: 100R; R_0805_2012Metric_Pad1.20x1.40mm_HandSolder
R16: R_Potentiometer_Trim; POT_3296W
R23: 360; R_0805_2012Metric_Pad1.20x1.40mm_HandSolder
T1: BFU590G; SOT-223
T2, T3, T5, T6, T7, T9: BFQ262; TO126AV
T4, T10, T11, T12: BFQ252; TO126AV
T8: SOT23_NXP
TP1, TP2, TP3, TP4, TP5, TP6, TP7: TestPoint; TestPoint_Pad_D1.0mm

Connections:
+5V: C5.1, D4.1 (K), R1.1, R2.1, R6.1, R15.1, R23.1, R31.2, TP6.1
+VDC: C6.1, C7.1, D3.1 (K), R11.1, R14.1, T5.2 (C), T6.2 (C), T7.2 (C), T9.2 (C), TP5.1
/+5V_IN: F2.2, J2.1
/+80V_IN: F1.2, J1.1
/F1: D3.2 (A), F1.1
/F2: D4.2 (A), F2.1
/FB1: D2.1 (A), R10.1, R13.2, T3.1 (E)
/FB2: Q2.2 (C), R6.2, R9.2, R30.2, TP1.1
/LED: J5.1, R23.2
GND: C1.2, C3.2, C4.2, C5.2, C6.2, C7.2, C10.2, C11.2, H1.1, J1.2, J2.2, J3.2, J4.S1, J5.2, Q1.1 (C), R4.2, R7.2, R16.3, T4.2 (C), T8.3 (C), T10.2 (C), T11.2 (C), T12.2 (C)
unnamed: C1.1, R8.2
unnamed: C2.2, D1.2 (A), Q1.2 (B), R2.2, TP7.1
unnamed: D2.3 (K), R11.2, T2.2 (C), T3.3 (B)
unnamed: Q1.3 (E), R1.2, R5.1, TP2.1
unnamed: Q2.4 (B), R5.2
unnamed: C4.1, Q2.1 (E), Q2.3 (e), R7.1, R8.1, TP3.1
unnamed: R9.1, R10.2
unnamed: R3.1, R13.1, R17.1, R18.1, R19.1
unnamed: R15.2, R16.1
unnamed: R30.1, T1.2 (B)
unnamed: T1.4 (C), T2.1 (E)
unnamed: C3.1, C11.1, T1.1 (E), T1.3 (e), T8.2 (E)
unnamed: C10.1, R31.1, T2.3 (B)
unnamed: R14.2, T3.2 (C)
unnamed: R3.2, T4.3 (B), T5.3 (B)
unnamed: R12.2, T4.1 (E), T5.1 (E)
unnamed: R16.2, T8.1 (B), TP4.1
unnamed: R17.2, T6.3 (B), T10.3 (B)
unnamed: R20.2, T6.1 (E), T10.1 (E)
unnamed: R18.2, T7.3 (B), T11.3 (B)
unnamed: R21.2, T7.1 (E), T11.1 (E)
unnamed: R19.2, T9.3 (B), T12.3 (B)
unnamed: R22.2, T9.1 (E), T12.1 (E)
input: C2.1, D1.1 (K), J3.1, R4.1
output: J4.1, R12.1, R20.1, R21.1, R22.1

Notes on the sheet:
Notes: check emitter pins Q2: extra caps? check size for 47ohm out Rs check size wattage R14 Why two FB resistors?

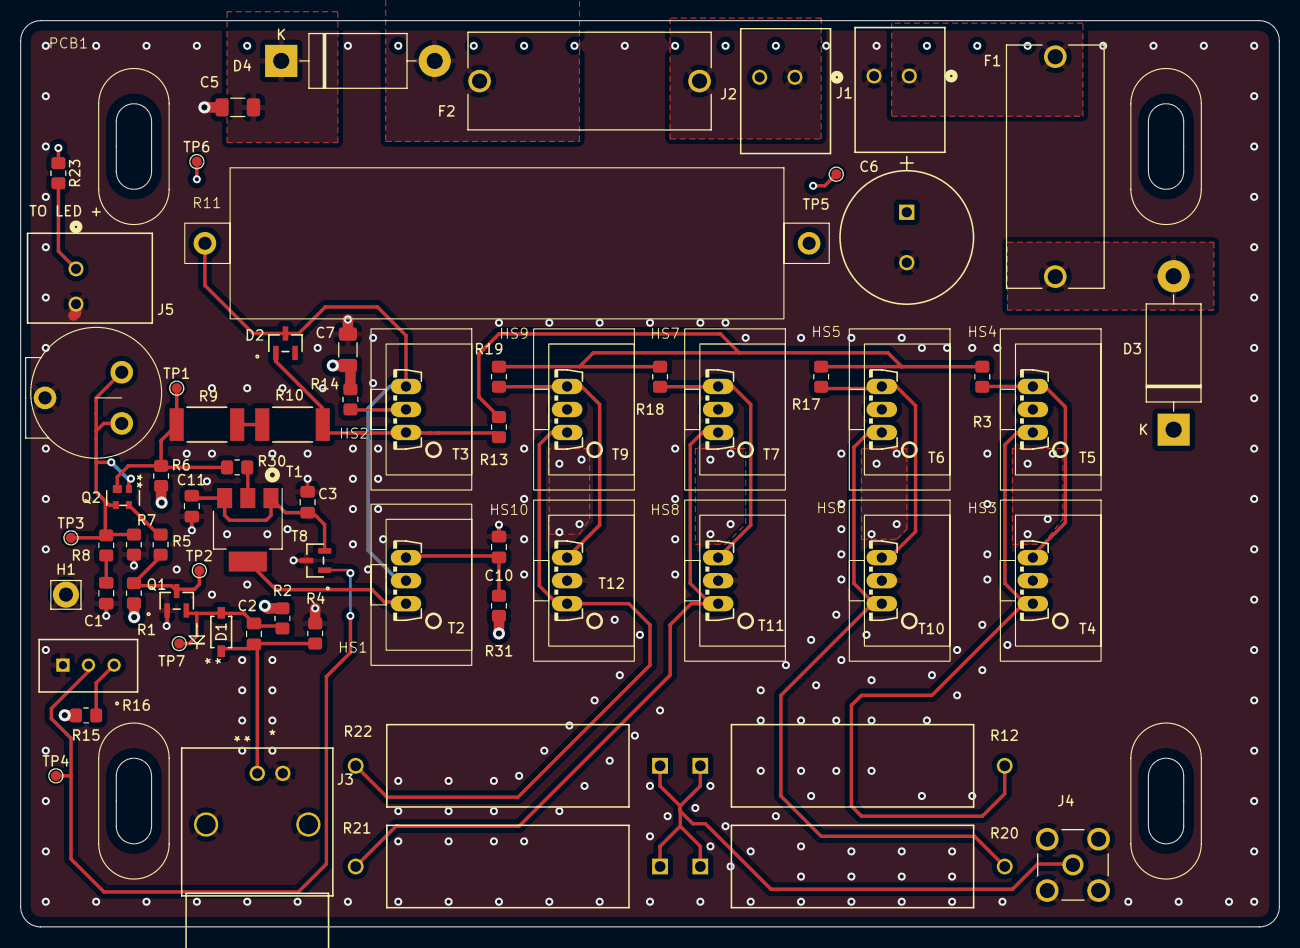
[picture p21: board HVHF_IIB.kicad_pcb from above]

Board: 4 copper layers, 125.0 x 90.0 mm, 79 parts (1 on the bottom side), 35 nets.

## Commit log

2024-05-22 Initial commit basics
    adds spice files and eagle initials and data sheets
    [HVHF_IIB.brd, HVHF_IIB.sch]
2024-05-25 First KiCad submit
    [HVHF_IIB.kicad_pcb, HVHF_IIB.kicad_sch]
2024-05-28 schematic work
    adds components
    some foot prints
    [HVHF_IIB.kicad_pcb, HVHF_IIB.kicad_sch]
2024-05-29 adds footprints
    [1984963.stp, 3296W-1-101RLF.step, 731375003.stp, CONSMA002-L.step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]
2024-05-29 adds footprints
    3d models
    [HVHF_IIB.kicad_pcb, HVHF_IIB.kicad_sch]
2024-05-29 wrapped up schematic
    placed and routed all components on schematic
    adds all footprints
    [CAP_EEUED_125X25_PAN.step, CR_BAS70-02V_INF.step, GRM31CR61A107MEA8L.step, HVHF_IIB.kicad_pcb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]
2024-05-31 PCB layout
    adds bard logo
    began pcb layout
    adds 3D model heat sink
    [ATS-PCB1025.step, HVHF_IIB.kicad_pcb, HVHF_IIB.kicad_sch, T0-126.step]
2024-05-31 board layout
    sourced all components
    laid out all components
    designed all 3D models
    [HVHF_IIB.kicad_pcb, HVHF_IIB.kicad_sch, PPZC80003.step, PWWR0016F330RK9 v2.step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]
2024-06-01 fixed Kicad error
    board already open error
    moved log files to Miscellaneous folder
    [HVHF_IIB-B_Cu.gbl, HVHF_IIB-B_Cu.gbr, HVHF_IIB-B_Mask.gbr, HVHF_IIB-B_Mask.gbs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]
2024-06-06 pcb work
    routing
    components
    net classes
    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
    [4527.step, HVHF_IIB.kicad_pcb, HVHF_IIB.kicad_sch, RES_3560_TEC.step]
2024-06-06 began routing
    [HVHF_IIB.kicad_pcb]
2024-06-07 pcb routing
    updated pcb brd footprint
    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
    [EC1U-AutoCADDXF.dxf, EC1U-Solidworks.sldprt, EC1U-Step.step, HVHF_IIB.kicad_pcb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]
2024-06-07 routing
    Did DRC
    Did ERC (some errors to fix)
    [HVHF_IIB.kicad_pcb, HVHF_IIB.kicad_sch]
2024-06-07 small fix to pcb silk
    [HVHF_IIB.kicad_pcb]
2024-06-08 fixed orientation error T4,T10-T12
    [HVHF_IIB.kicad_pcb, HVHF_IIB.kicad_sch, RES_ALSR05_VIS.step]
2024-06-08 fixed unconnected GND power pin
    [HVHF_IIB.kicad_sch]
2024-06-08 fixes, adds, silk
    fixed Q1 rotation
    adds LED
    adds GND
    [HVHF_IIB.kicad_pcb, HVHF_IIB.kicad_sch]
2024-06-10 trace length matching
    [HVHF_IIB.kicad_pcb, HVHF_IIB.kicad_sch, SOT-23_ONS.step]
2024-06-10 Post DR
    [HVHF_IIB.kicad_pcb, HVHF_IIB.kicad_sch]
2024-06-14 stitching done
    [EO-PM-NR-C4-AutoCADDXF.dxf, EO-PM-NR-C4-Solidworks.sldprt, HVHF_IIB.kicad_pcb, HVHF_IIB.kicad_sch]
2024-06-14 checked footprints
    [HVHF_IIB.kicad_pcb, HVHF_IIB.kicad_sch, SOT23_INF.step, SOT23_NXP.step]
2024-06-17 JLC SUBMIT 6/17/2024
    [HVHF_IB_BOM.xlsx, HVHF_IIB-B_Cu.gbl, HVHF_IIB-B_Cu.gbr, HVHF_IIB-B_Mask.gbr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]
2024-06-19 added build/production files submit 1-6/19
    [HVHF_IB_BOM.xlsx, HVHF_IIB-top-pos.csv, HVHF_IIB.csv]
2024-06-19 BOM updates
    [HVHF-IIB-01_JLC_CPL.xlsx, HVHF_IB_BOM.xlsx, HVHF_IIB-top-pos.csv, HVHF_IIB.csv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]
